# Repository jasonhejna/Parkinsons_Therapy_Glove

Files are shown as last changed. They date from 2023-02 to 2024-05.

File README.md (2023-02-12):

# Parkinsons_Therapy_Glove
Open Source Hardware design for Vibrotactile Coordinated Reset (vCR) Gloves.

open source hardware logo

# Intro

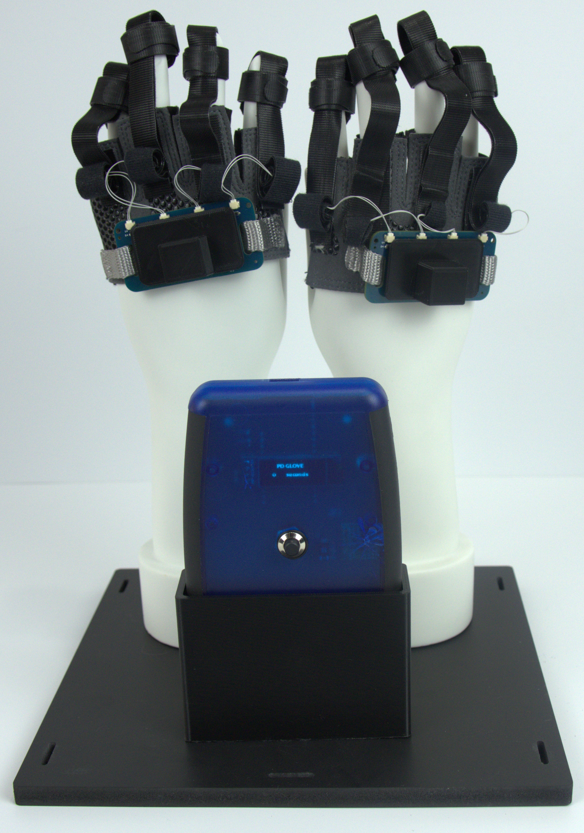
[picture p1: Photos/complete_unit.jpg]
Project Photo


Abnormal synchronization of neuronal activity in dopaminergic circuits is related to motor impairment in Parkinson’s disease (PD). Vibrotactile coordinated reset (vCR) fingertip stimulation aims to counteract excessive synchronization and induce sustained unlearning of pathologic synaptic connectivity and neuronal synchrony.

Vibrotactile Coordinated Reset delivers vibratory stimulation to the fingertips of each hand. A specific pattern of vibration to each fingertip is delivered which theoretically disrupts abnormal synchrony in the brain.

This project provides instructions to build your own vCR Glove. Including Bill of Materials, Instructions, CAD Files, Circuit Board design files, and Firmware.

# Control Box

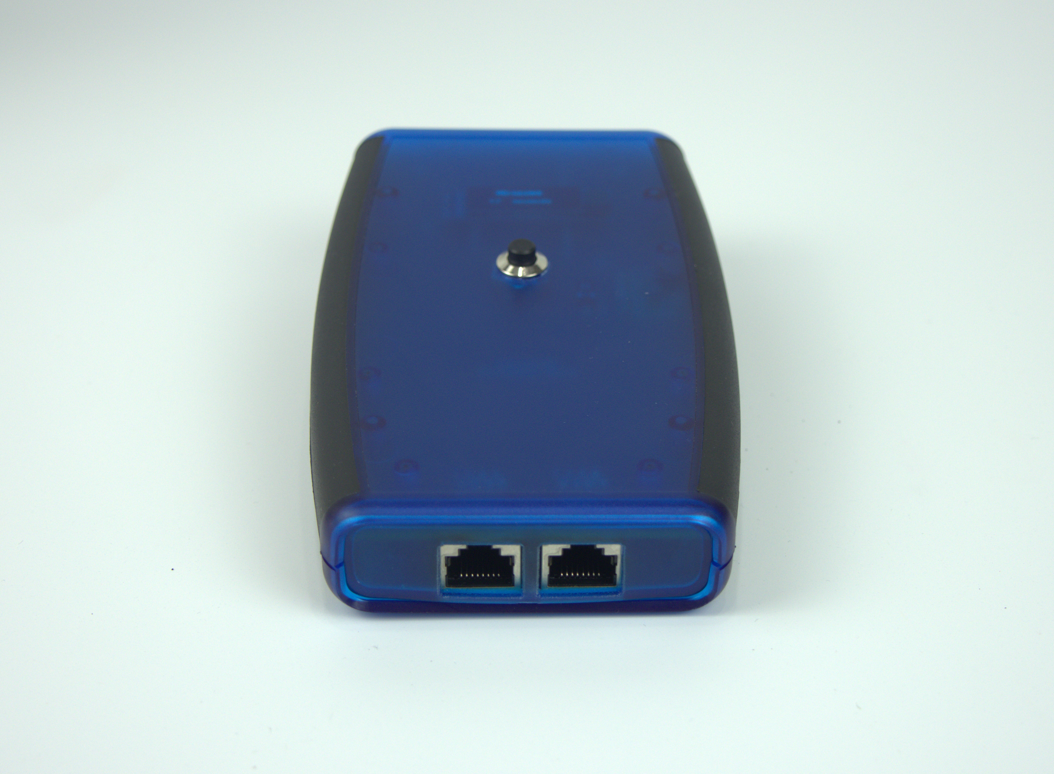
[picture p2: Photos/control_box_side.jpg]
Project Photo

Project Photo
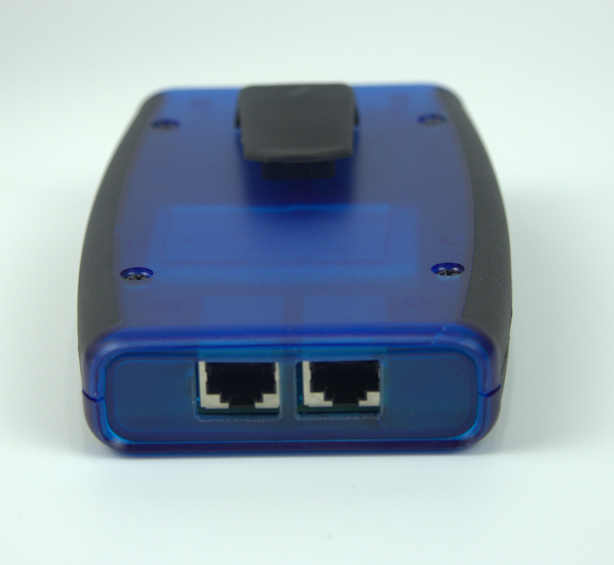
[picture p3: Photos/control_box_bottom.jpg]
Project Photo

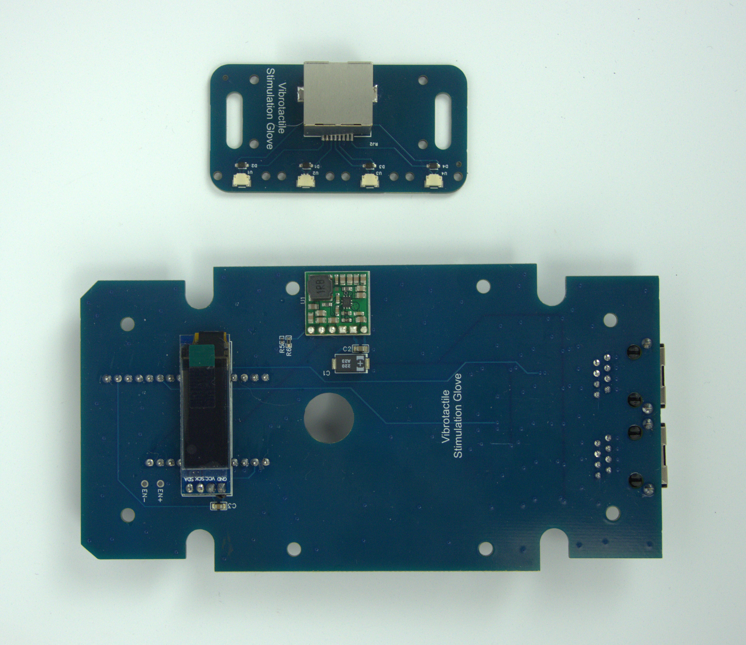
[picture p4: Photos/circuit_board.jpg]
Project Photo

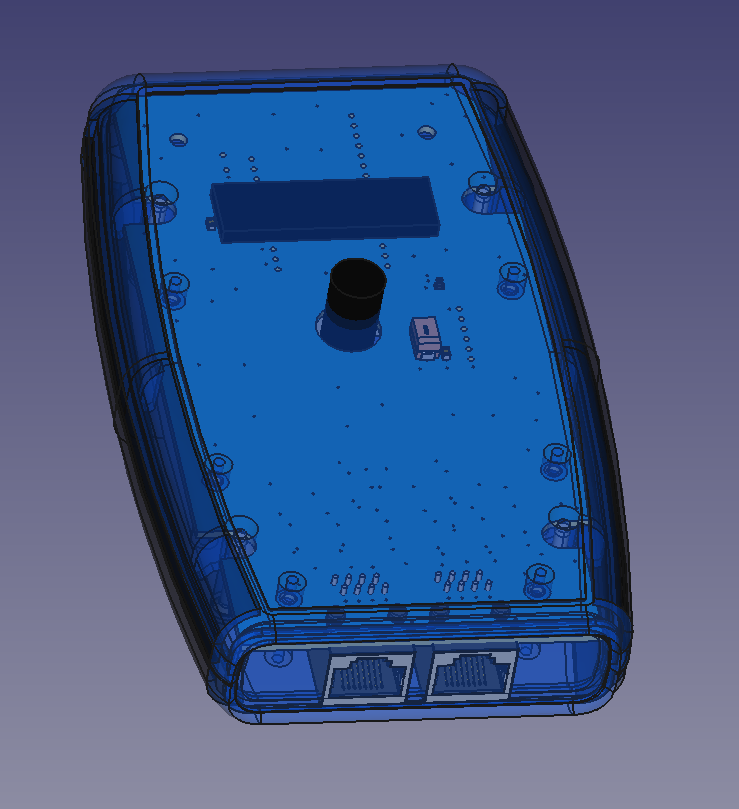
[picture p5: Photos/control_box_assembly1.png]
Project Photo

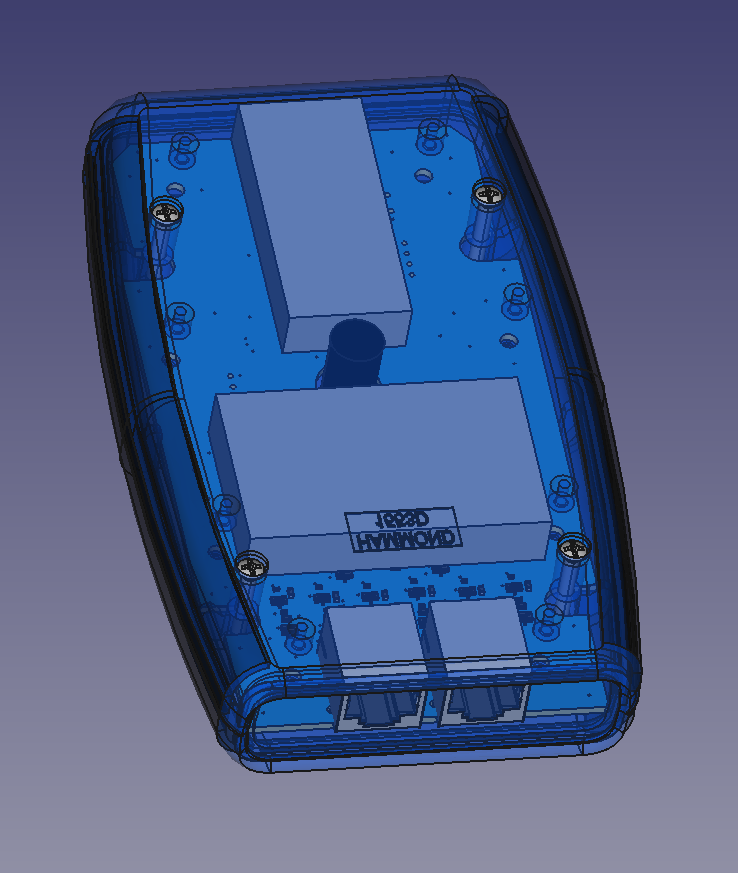
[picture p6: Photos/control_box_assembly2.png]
Project Photo

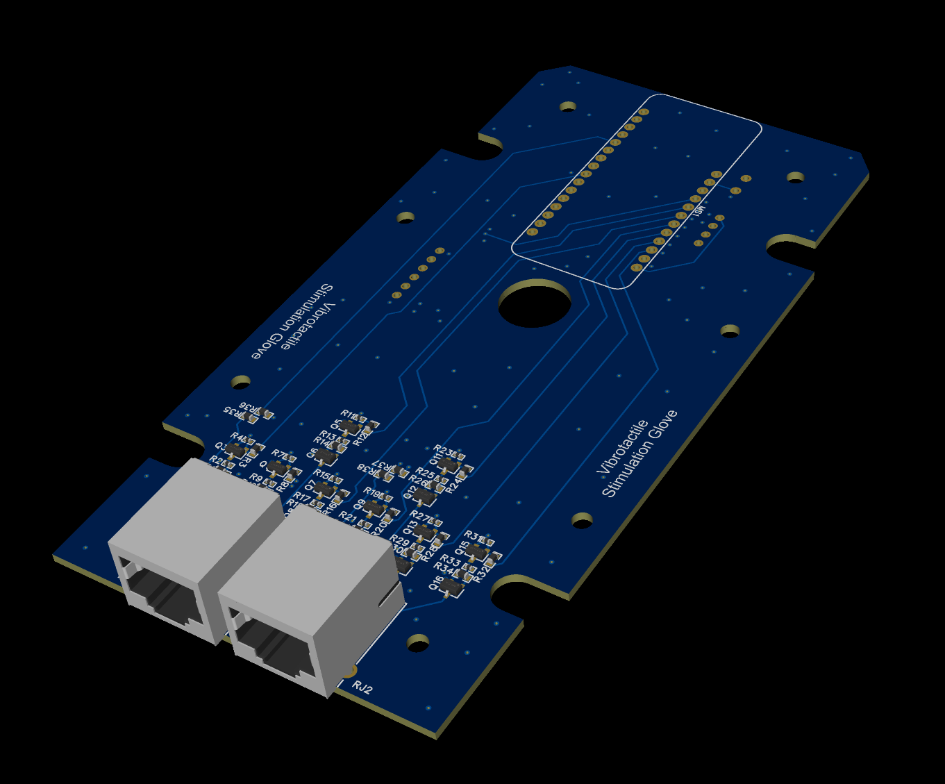
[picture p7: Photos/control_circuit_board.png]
Project Photo


## Build Steps
1) You will need to have a manufacturer create the Printed Circuit Boards (PCB). Upload the Gerber file to the manufacturer: Control_Box\Electronics\Control_Box_Gerber.zip.  I recommend having your circuit board assembled with all the components. Use the PickAndPlace, and BOM files for assembly. JLCPCB.com is a good choice for manufacturer.
2) You will also need to order parts. See the Bill of Materials.
3) You will need to solder on the Feather Microcontroller, Screen, and Boost Converter. These parts are easy to solder 2.54 through hole components.
4) You will need to solder on the switch to the two pins labeled EN+ and EN-.
5) You will need to cut a hole for the switch, and cut a slot for the USB charging cable. These cuts may be made with hand tools. You may also find laser cutter dxf files in Control_Box/Case_Assembly.
6) You will need to flash the provided firmware onto the Feather Microcontroller. Use the Arduino IDE and a USB cable. See Firmware.

## Hardware Bill of Materials
|Part|Part #|Quantity|Manufacturer|URL|
|----|----|----|----|----|
|Custom Printed Circuit Board (See Control_Box/Electronics for design files) ||1|JLCPCB|https://jlcpcb.com/|
|Panel Mount Latching Push Button|CYT1091|1|Cylewet|https://www.amazon.com/Cylewet-Self-Locking-Latching-Button-CYT1091/dp/B075VBV4QH/ref=sr_1_3?keywords=Latching+Switch&qid=1673285409&sr=8-3|
|Case|1553D|1|Hammond Manufacturing|https://www.digikey.com/en/products/detail/hammond-manufacturing/1553DTBUBK/2094890|
|Belt Clip|1599CLIP|1|Hammond Manufacturing|https://www.digikey.com/en/products/detail/hammond-manufacturing/1599CLIP/460760|
|Boost Converter|U3V40F5|1|Pololu|https://www.pololu.com/product/4012|
|0.91 inch OLED LCD Display 128x32|SSD1306|1|Teyleten|https://www.amazon.com/Teyleten-Robot-Display-SSD1306-Raspberry/dp/B08ZY4YBHL/ref=asc_df_B08ZY4YBHL/?tag=hyprod-20&linkCode=df0&hvadid=647248209079&hvpos=&hvnetw=g&hvrand=3522876089040420258&hvpone=&hvptwo=&hvqmt=&hvdev=c&hvdvcmdl=&hvlocint=&hvlocphy=9010937&hvtargid=pla-1597285851745&psc=1&region_id=972485&gclid=CjwKCAiArY2fBhB9EiwAWqHK6iJZr7Km3gjcYjdACghR9q-pTSBiGfFTmBRAXwzSj8zmCsqIJq6RdxoCsYEQAvD_BwE
|Arduino based Feather Microcontroller|2772|1|Adafruit|https://www.adafruit.com/product/2772|
|Battery|2011|1|Adafruit|https://www.adafruit.com/product/2011|
|Screws for holding the Circuit Board|M3 x 8mm|6|Generic||
|Double Sided Adhesive|||Generic||

Note: the battery is necessary for operation.

# Glove Hardware

Project Photo
Project Photo
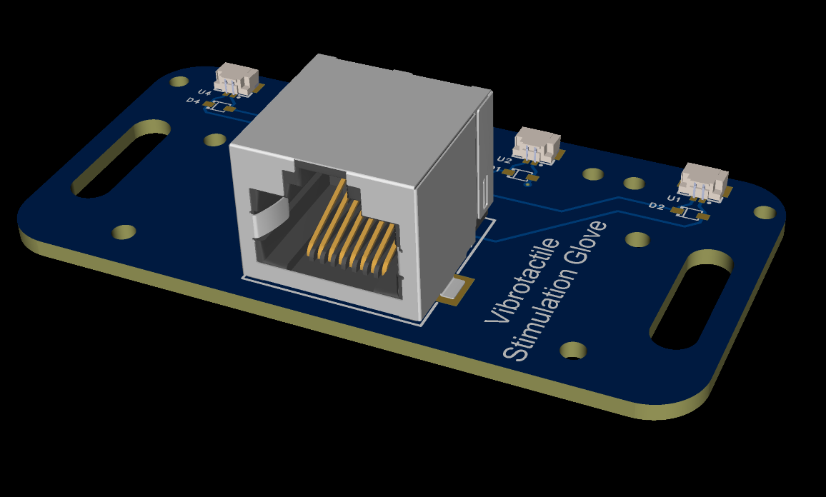
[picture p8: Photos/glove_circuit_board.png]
Project Photo


## Build Steps
1) You will need to send the Printed Circuit Board (PCB) design files to a manufacturer. I recommend having your circuit board assembled with all the components. Upload the Gerber file to the manufacturer (Glove_Hardware/Electronics/Glove_Gerber.zip).
2) Create cables by soldering or crimping the JST Cables onto the ERM Vibration Motor cables. You will need to make eight cable/motor assemblies.
3) Create the motor/finger mounts. This uses double sided velcro stips. The ERM Vibration Motor and cable is placed between two strips, and sewed at the ends. A third piece of velcro strip is used around the finger to ensure a snug fit. You will need to make 8 motor/finger mounts.
4) Cut and attach velcro strips to the glove so that they align with each finger on the glove. Recommend sewing the velcro strips to the gloves, and using adhesive.
5) Leaving extra length for hand movements. Using 1/2-inch Paracord, sew the circuit board to the gloves.
6) Plug the cable assemblies into to the circuit board.
7) Plug an ethernet cable between the glove and control box.
8) Optional. You can 3D print covers for the circuit boards. See Glove_Hardware/glove_PCB_cover.stl.

## Bill of Material

|Part|Part #|Quantity|Manufacturer|URL|
|----|----|----|----|----|
|Custom Printed Circuit Board (See Control_Box/Electronics) ||2|JLCPCB|https://jlcpcb.com/|
|ERM Vibration Motor|1637|8|Pololu|https://www.pololu.com/product-info-merged/1637|
|JST Cables|A02SUR02SUR32W152A|8|JST|https://www.digikey.com/en/products/detail/jst-sales-america-inc/A02SUR02SUR32W152A/6009353|
|Fingerless gloves|F019-BK-M|1|Fit Four|https://www.amazon.com/dp/B06X6NCYP1?psc=1&ref=ppx_yo2ov_dt_b_product_details|
|1/2-inch Paracord|10 X FLTNYLWEB12-SILVER|1|PARACORD PLANET|https://www.amazon.com/dp/B08DZ5GG8W?psc=1&ref=ppx_yo2ov_dt_b_product_details|
|Velcro Strips|91140|1|Velcro Brand|https://www.amazon.com/dp/B001E1Y5O6?psc=1&ref=ppx_yo2ov_dt_b_product_details|
|Ethernet Cable| |2|UGREEN|https://www.amazon.com/dp/B0875NB89J?psc=1&ref=ppx_yo2ov_dt_b_product_details|
|Thread for Sewing| |1|Generic| |
|Adhesive| |1|Generic| |

# Display Case (optional)

Project Photo

## Build Steps
1) Assemble the case using the provided components.
2) Mount the Mannequin Hand Display Stands to the board. I used two screws in each hand.
3) There is a stand for the Control Box which can be 3D printed. See Display_Case_Hardware\control_box_holder.stl. I used three screws to mount the control box holder.

## Bill of Materials

|Part|Part #|Quantity|Manufacturer|URL|
|----|----|----|----|----|
|Mannequin Hand Display Stands| |1|Taotenish|https://www.amazon.com/dp/B07YR2G1NX?psc=1&ref=ppx_yo2ov_dt_b_product_details|
|Display Case|8x8x12 inch 20x20x30 cm|1|KOLIPI|https://www.amazon.com/dp/B0B3WMXPKL?ref=ppx_yo2ov_dt_b_product_details&th=1|

# Editors
You may edit the Electronic design files using a PCB editing software called easyEDA. This project can be accessed on EasyEDA at: https://pro.easyeda.com/editor#id=4203400eb7db434e9a89eb5de0ddfd4a

The CAD files are in FreeCAD format and published in the /Control_Box and /Glove_Assembly folders.

# Attribution

The construction of this project would not be possible without the hard work and dedication of the research team that created Vibrotactile coordinated reset (vCR), conducted the research, and generally worked on this endeavor.

# Author

* Jason Hejna - Product Development Engineer

# Final Thoughts

All design files are provided completely free of charge. I welcome any feedback or improvements to the design. Please submit feedback through Github.

Please notify me if parts go out of stock. I would like to update out of stock parts.

To anyone who tries this design. Please let me know how it goes!

Thank you

# License

This source code is licensed under the Apache-2.0 license found in the LICENSE file in the root directory of this source tree. This project should be considered Open Source Hardware. You are free to use and modify any of the content herein.

Unless otherwise separately undertaken by the Licensor, to the extent possible, the Licensor offers the Licensed Material as-is and as-available, and makes no representations or warranties of any kind concerning the Licensed Material, whether express, implied, statutory, or other. This includes, without limitation, warranties of title, merchantability, fitness for a particular purpose, non-infringement, absence of latent or other defects, accuracy, or the presence or absence of errors, whether or not known or discoverable. Where disclaimers of warranties are not allowed in full or in part, this disclaimer may not apply to You.

To the extent possible, in no event will the Licensor be liable to You on any legal theory (including, without limitation, negligence) or otherwise for any direct, special, indirect, incidental, consequential, punitive, exemplary, or other losses, costs, expenses, or damages arising out of this Public License or use of the Licensed Material, even if the Licensor has been advised of the possibility of such losses, costs, expenses, or damages. Where a limitation of liability is not allowed in full or in part, this limitation may not apply to You.

The disclaimer of warranties and limitation of liability provided above shall be interpreted in a manner that, to the extent possible, most closely approximates an absolute disclaimer and waiver of all liability.

open source hardware logo

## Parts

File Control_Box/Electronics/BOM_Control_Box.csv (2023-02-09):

No. | Quantity | Comment | Designator | Footprint | Value | Manufacturer Part | Manufacturer | Supplier Part | Supplier | LCSC Price | LCSC Stock | JLCPCB Price | JLCPCB Stock | Datasheet | Device | JLCPCB Part Class | LCSC Part Name | Name | Unique ID | Resistance | link
1 | 1 | 220uF | C1 | CAP-SMD_L7.3-W4.3-FD |  | 10TPB220M | PANASONIC(松下) | C242173 | LCSC | 1.4812 | 1149 | 9.31 | 557 |  | 10TPB220M | Extended Part |  | 220uF | ggefb66db9da985fa0a
2 | 2 | 2.2uF | C2,C3 | C0805 |  | CL21A225KAFNNNE | SAMSUNG(三星) | C87994 | LCSC | 0.0170 | 820911 | 0.107 | 385176 |  | CL21A225KAFNNNE | Extended Part |  | 2.2uF | gge1a06ba7d37b3afd1,gge46e4a037fbfb9242
3 | 1 | OLED-128x32 | EKRAN1 | OLED-128X32 |  |  |  |  |  |  |  |  |  |  | OLED-128x32 |  |  | OLED-128x32 | gge044529670250cb18
4 | 1 | FEATHERWING_NOSCREW | MS1 | FEATHERWING_NO_SCREW |  |  |  |  |  |  |  |  |  |  | FEATHERWING_NOSCREW |  |  | FEATHERWING_NOSCREW | gge0b1f5ab786c41376
5 | 8 | MMBT3904_C84104 | Q1,Q3,Q5,Q7,Q9,Q11,Q13,Q15 | SOT-23-3_L2.9-W1.3-P1.90-LS2.4-BR |  | MMBT3904 | ST(先科) | C84104 | LCSC |  |  | 0.0602 | 14817 |  | MMBT3904 | Extended Part |  | MMBT3904_C84104 | gge0d8f3384ea90c7eb,gge7a08e0e46a781eb4,gge478dc22ffe3ca8c7,gge4665e3497868fa47,gge14039e7fc573214c,gged5d5b23e4e6ef882,ggee2e4628fe4e2b352,ggef5bf92d5a9ef5d9f
6 | 8 | SI2301CDS-T1-GE3 | Q2,Q4,Q6,Q8,Q10,Q12,Q14,Q16 | SOT-23-3_L3.0-W1.7-P0.95-LS2.9-BR |  | SI2301CDS-T1-GE3 | VISHAY(威世) | C10487 | LCSC |  |  | 0.486 | 152709 |  | SI2301CDS-T1-GE3 | Basic Part |  | SI2301CDS-T1-GE3 | gge3ea9f58e1a9d2235,gge38e5560dc2c3958e,gge0185c38df4925a71,gge32537c7c1aede5f6,gge98106f643687806a,gge679073baed65af24,ggec29e948761800ac1,ggeea604fc2c4f0d98f
7 | 8 | 5.1kΩ | R1,R10,R14,R18,R22,R26,R30,R34 | R0603 |  | 0603WAF5101T5E | UNI-ROYAL(厚声) | C23186 | LCSC |  |  | 0.00612 | 2346929 |  | 0603WAF5101T5E | Basic Part |  | 5.1kΩ | gge0e08dae5721967aa,gge1eebddf9433234d1,gge2c73753931f9d155,gge2f105896c2ffab49,gge0569ea8743deffbf,ggeaa26469ff685048f,ggeb6967aa3b093cba2,ggec5a22d11ef3ee535 | 5.1K
8 | 8 | 240 | R2,R9,R13,R17,R21,R25,R29,R33 | R0402 |  | RC0402FR-07240RL | YAGEO(国巨) | C114755 | LCSC | 0.0007 | 894213 | 0.00397 | 439205 |  | RC0402FR-07240RL | Extended Part |  | 240 | gge0dd8dcd77110c2b5,ggea412932cabd9c5ae,ggeb774cabebffb13fc,ggec9dba533525f9deb,ggee83e79d6018652b2,ggee234d4903c11e999,ggee3874f5411e3afd0,ggef620bca2e64ef807 | 240Ω
9 | 8 | 1K | R3,R8,R12,R16,R20,R24,R28,R32 | R0603 |  | RC0603FR-071KL | YAGEO(国巨) | C22548 | LCSC |  |  | 0.0064 | 8842618 |  | RC0603FR-071KL | Extended Part |  | 1K | gge0a6abd6e610a20c9,gge2ded78ec2fb9edbc,gge80f93691236e084b,gge064419a47c78d1c7,ggeb1a6cf13fe8cc19d,ggeb491da9607a06c68,ggedd7d89d986fabf59,ggefbf9b83a19b411b1 | 1kΩ
10 | 8 | 6.8K | R4,R7,R11,R15,R19,R23,R27,R31 | R0402 |  | RC0402JR-076K8L | YAGEO(国巨) | C137847 | LCSC | 0.0027 | 501094 | 0.0168 | 499473 |  | RC0402JR-076K8L | Extended Part |  | 6.8K | gge626e64a32193c4d6,gge6251308beb247644,ggea1c0f7c11c7a8d0c,ggeaf5e3272f7eed8d0,ggeb20474b0b163cf00,ggee325568edbf406da,ggee031622812261daa,ggef78691cabab940e6 | 6.8kΩ
11 | 1 | 1kΩ | R5 | R0402 |  | ERJ2RKF1001X | PANASONIC(松下) | C242161 | LCSC |  |  | 0.0379 | 82769 |  | ERJ2RKF1001X | Extended Part |  | 1kΩ | gge365197d47bb9c1b3 | 1K
12 | 1 | 100kΩ | R6 | R0603_NEW |  | ERJ3EKF1003V | PANASONIC(松下) | C189597 | LCSC | 0.0078 | 242750 | 0.0487 | 68654 |  | ERJ3EKF1003V | Extended Part |  | 100kΩ | ggeff73743931110229 | 100K
13 | 2 | 47kΩ | R35,R38 | R0603 |  | 0603WAF4702T5E | UNI-ROYAL(厚声) | C25819 | LCSC |  |  | 0.00657 | 1968208 |  | 0603WAF4702T5E | Basic Part |  | 47kΩ | gge40aad60bb57603be,gge06469131e3f9cd7b | 47K
14 | 2 | 33K | R36,R37 | R0603 |  | RC0603FR-0733KL | YAGEO(国巨) | C126359 | LCSC | 0.0012 | 512800 | 0.00749 | 249861 |  | RC0603FR-0733KL | Extended Part |  | 33K | gge35f5d87f0bcb1737,ggef8a6432b7912eec9 | 33kΩ
15 | 2 | R-RJ45R10P-B000 | RJ1,RJ2 | RJ45-TH_R-RJ45R10P-B000 |  | R-RJ45R10P-B000 | Shenzhen Cankemeng | C386758 | LCSC | 0.2627 |  | 1.651 | 0 |  | R-RJ45R10P-B000 | Extended Part |  | R-RJ45R10P-B000 | ggea55be19a1e3e3d3d,ggeb44bf9b5ea99e3c0
16 | 1 | U3V40F5 | U1 | U3V40F5 |  | U3V40F5 | Pololu | U3V40F5 |  |  |  |  | 0 |  | U3V40F5 |  |  | U3V40F5 | gge4cbcb20c9828dc29 |  | https://www.pololu.com/product/4012
17 | 2 | WIRE_SOLDER_POINT | U2,U3 | WIRE_SOLDER_POINT |  |  |  |  |  |  |  |  |  |  | WIRE_SOLDER_POINT |  |  | WIRE_SOLDER_POINT | gge8aa853f11ac9839f,ggef3f20beaa0858562

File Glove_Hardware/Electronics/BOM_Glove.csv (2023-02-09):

No. | Quantity | Comment | Designator | Footprint | Value | Manufacturer Part | Manufacturer | Supplier Part | Supplier | LCSC Price | LCSC Stock | JLCPCB Price | JLCPCB Stock | Datasheet | Device | JLCPCB Part Class | LCSC Part Name | Name | Unique ID | Resistance | link
1 | 4 | 1N4148WS T4 | D1,D2,D3,D4 | SOD-323_L1.8-W1.3-LS2.5-RD |  | 1N4148WS | CJ(江苏长电/长晶) | C2128 | LCSC |  |  | 0.0667 | 7820304 |  | 1N4148WS | Basic Part |  | 1N4148WS T4 | gge6,gge7,gge8,gge9
2 | 1 | MJ5688-B111-HR1-C | RJ2 | RJ45-TH_MJ5688-B111-HR1-C |  | MJ5688-B111-HR1-C | Heling(合陵) | C501471 | LCSC | 0.6539 | 734 | 4.11 | 205 | https://atta.szlcsc.com/upload/public/pdf/source/20200325/C501471_CCCA8890611B7886CC8D3331CE0DA9EE.pdf | MJ5688-B111-HR1-C | Extended Part | RJ45 卧贴 不带LED 全包反口 | MJ5688-B111-HR1-C | gge5
3 | 4 | SM02B-SURS-TF(LF)(SN) | U1,U2,U3,U4 | CONN-SMD_SM02B-SURS-TF-LF-SN |  | SM02B-SURS-TF(LF)(SN) | JST | C566239 | LCSC | 0.2409 | 26995 | 1.514 | 10245 | https://atta.szlcsc.com/upload/public/pdf/source/20200826/C566239_A8FBB14050B915565F3B5D1E0D0D12F8.pdf | SM02B-SURS-TF(LF)(SN) | Extended Part | 针座 | SM02B-SURS-TF(LF)(SN) | gge1,gge2,gge3,gge4

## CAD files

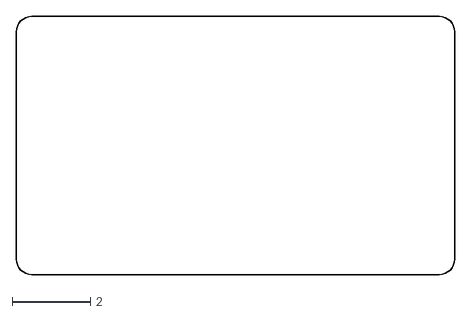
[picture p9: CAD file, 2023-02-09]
Control_Box/Case_Assembly/usb.dxf
11.2 x 6.60

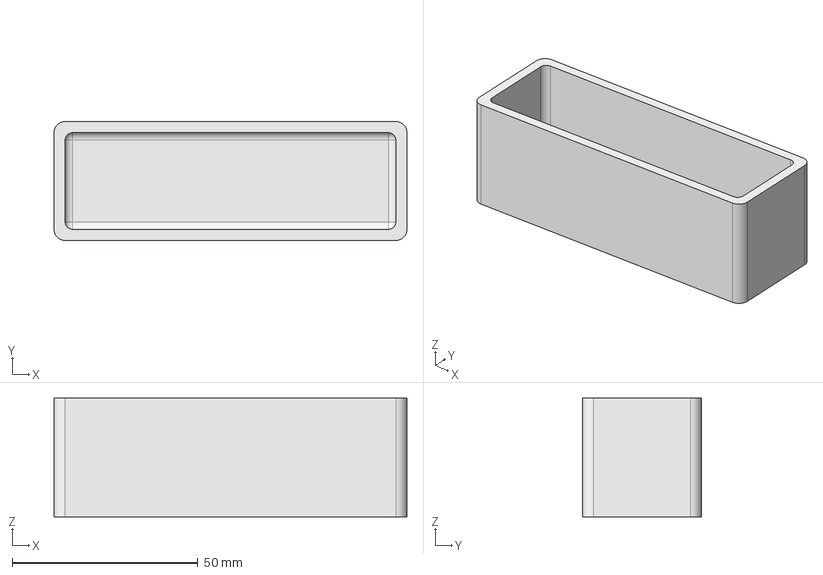
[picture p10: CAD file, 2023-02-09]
Display_Case_Hardware/control_box_holder.FCStd
95.0 x 32.0 x 32.0 mm

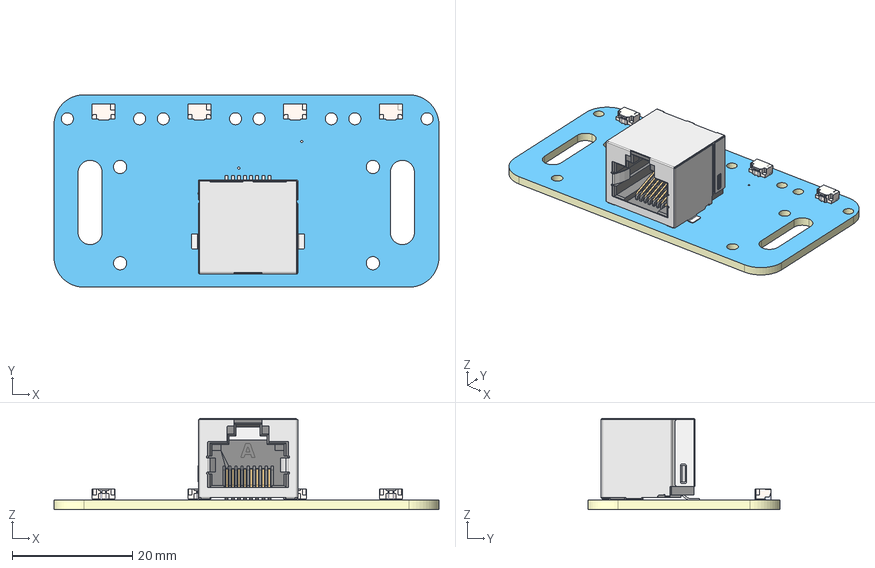
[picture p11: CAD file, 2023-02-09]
Glove_Hardware/Glove_Assembly/3D_PCB2_2023-01-24.step
64.0 x 32.0 x 15.2 mm

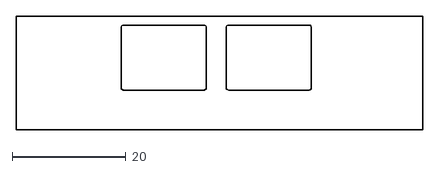
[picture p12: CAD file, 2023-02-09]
Control_Box/Case_Assembly/ethernet.dxf
71.6 x 20.0

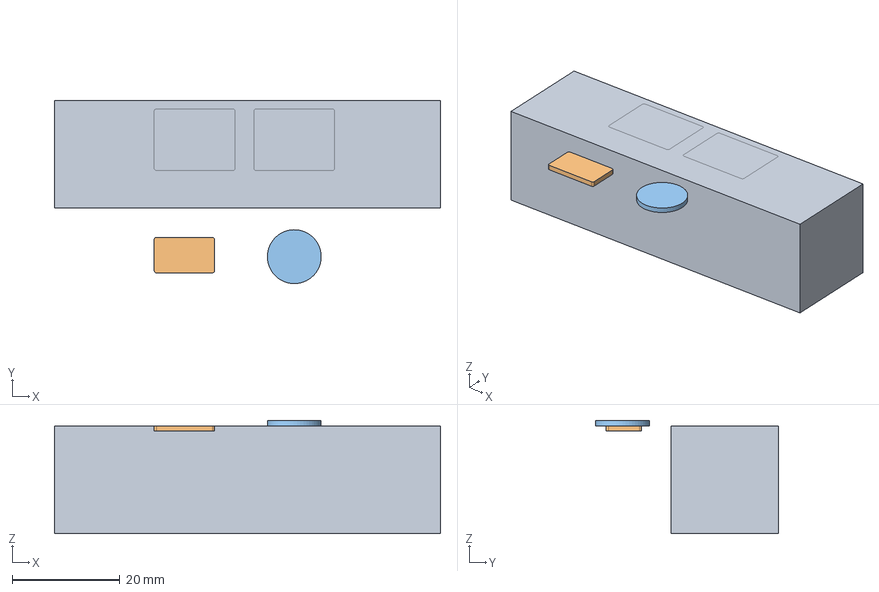
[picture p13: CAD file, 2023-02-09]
Display_Case_Hardware/laser_cut_files.FCStd
71.6 x 34.0 x 21.0 mm
ethernet
usb
switch

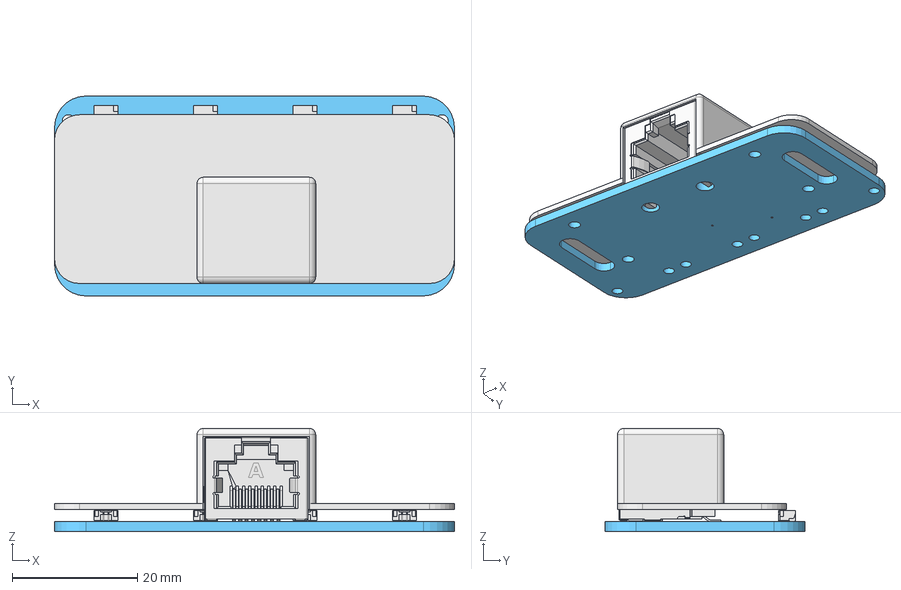
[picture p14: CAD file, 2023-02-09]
Glove_Hardware/Glove_Assembly/glove_top.FCStd
64.0 x 32.0 x 16.5 mm

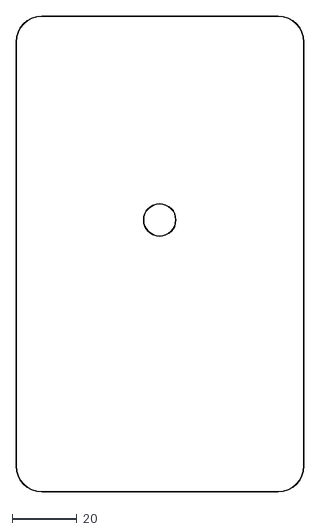
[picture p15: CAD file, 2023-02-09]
Control_Box/Case_Assembly/button.dxf
89.2 x 147.3

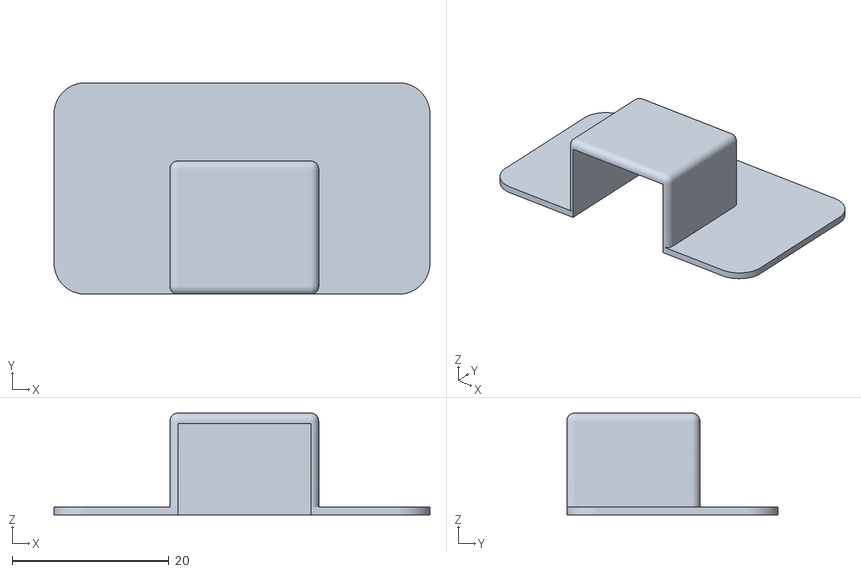
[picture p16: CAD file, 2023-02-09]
Glove_Hardware/Glove_Assembly/glove_PCB_cover.stl
48.0 x 27.0 x 13.0

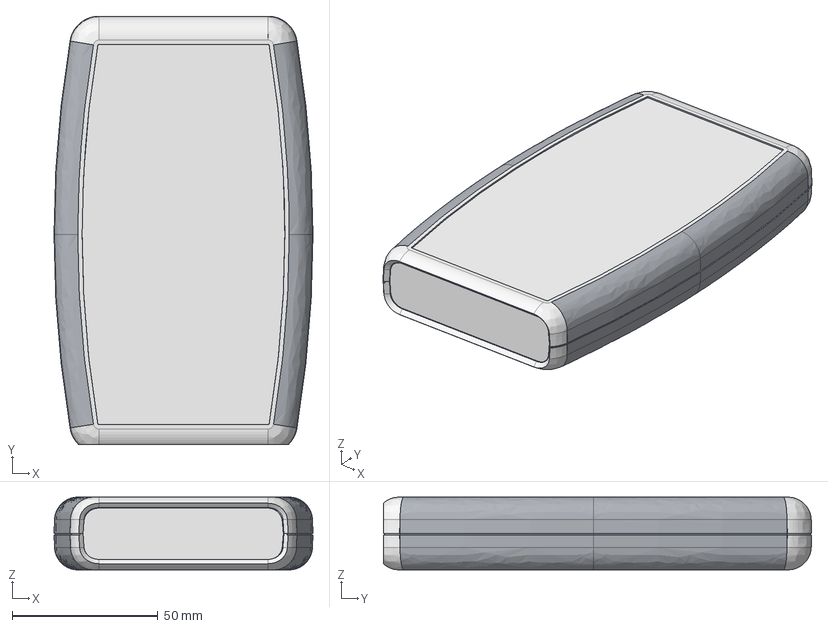
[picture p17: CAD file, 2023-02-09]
Control_Box/Case_Assembly/1553D.stp
89.0 x 147.2 x 25.0 mm
1553D BOTTOM
1553D TOP
1553D FRONT PANEL
1553D PCB
1553D BOTTOM GRIP
1553D TOP GRIP

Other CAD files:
Display_Case_Hardware/control_box_holder.stl

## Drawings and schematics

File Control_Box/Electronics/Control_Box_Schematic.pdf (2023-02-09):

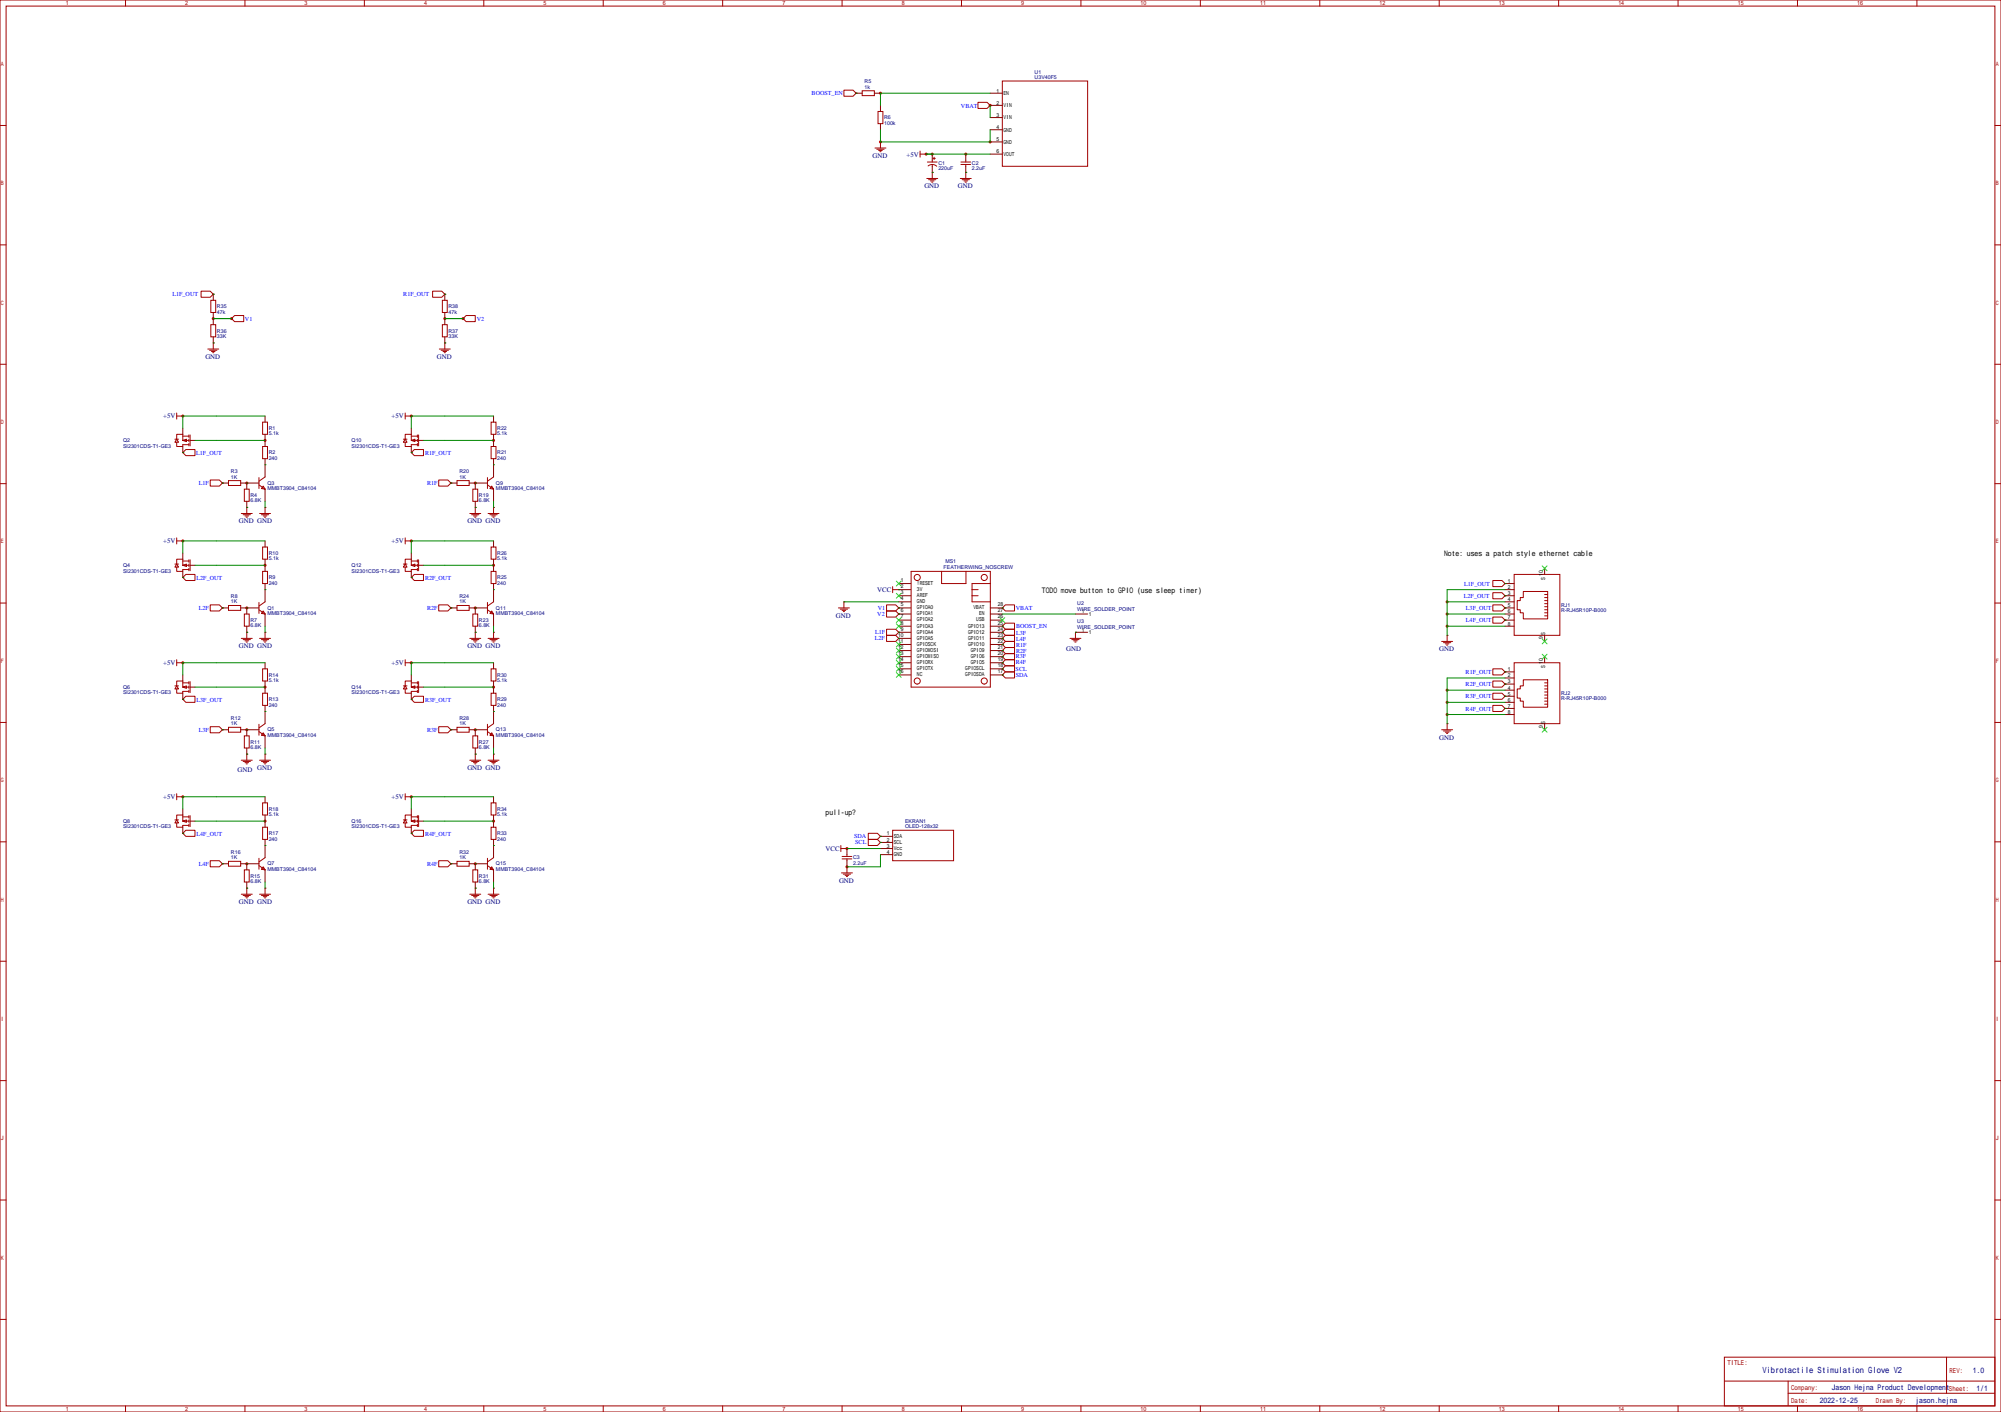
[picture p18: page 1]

Note: uses a patch style ethernet cable

TODO move button to GPIO (use sleep timer)

Jason Hejna Product Development

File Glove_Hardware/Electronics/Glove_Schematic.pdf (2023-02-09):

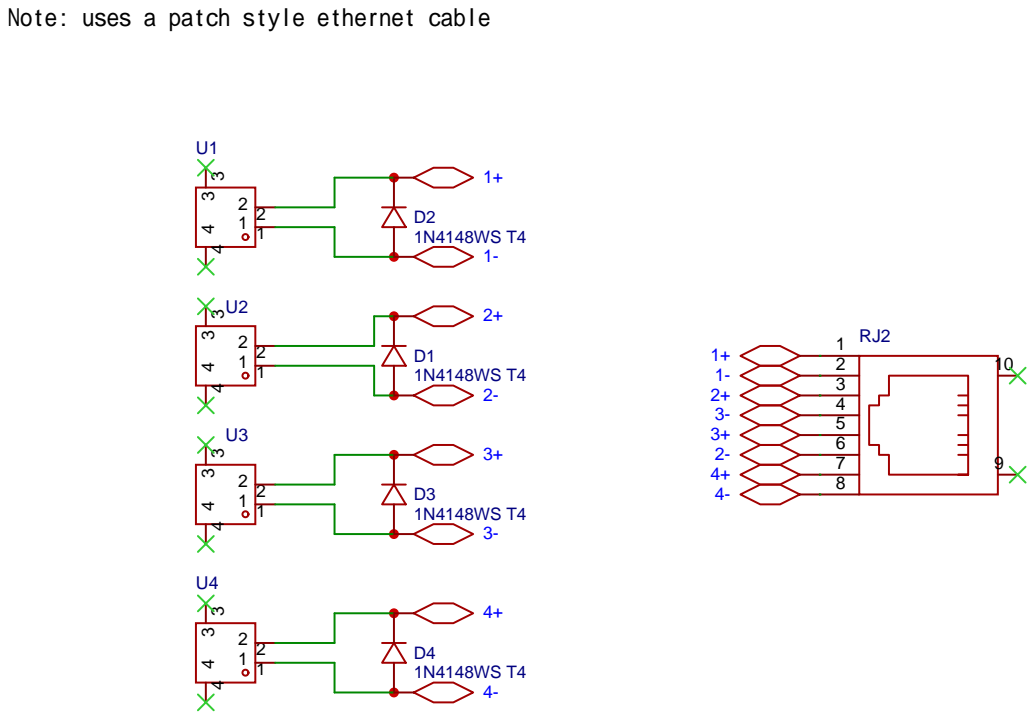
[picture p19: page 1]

Note: uses a patch style ethernet cable

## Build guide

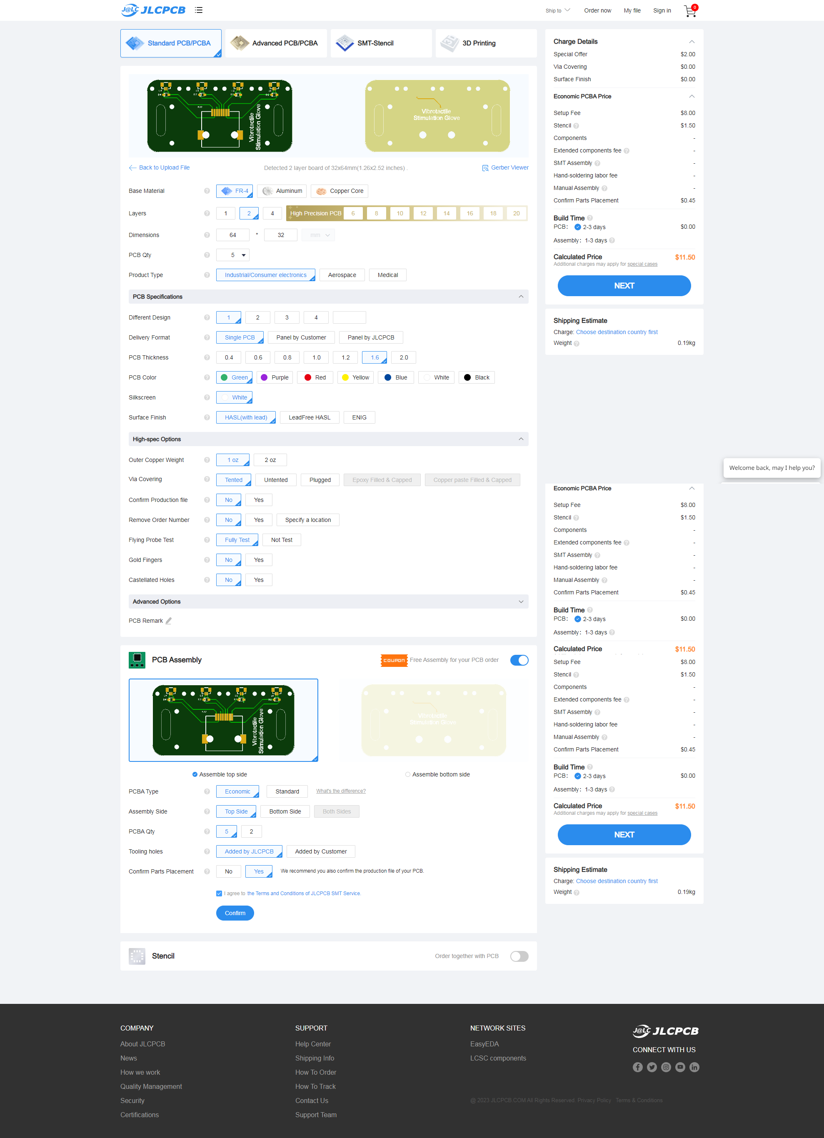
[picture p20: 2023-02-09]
Glove_Hardware/Electronics/jlcpcb_fabrication_settings.png

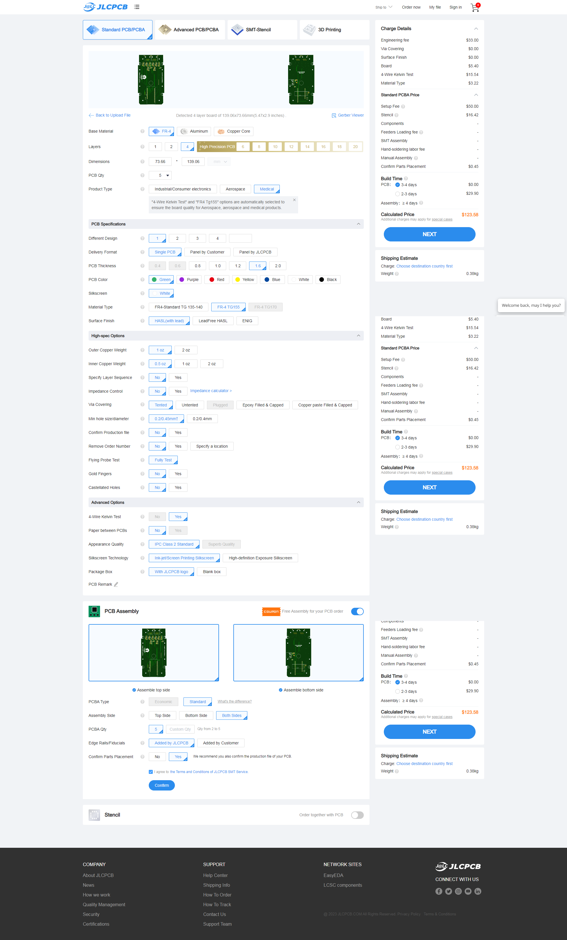
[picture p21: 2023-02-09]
Control_Box/Electronics/jlcpcb_fabrication_settings_control_box.png

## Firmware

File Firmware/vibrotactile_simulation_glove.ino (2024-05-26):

/*
 * Copyright (c) 2023, Jason Hejna
 * All rights reserved.
 * 
 * This source code is licensed under the Apache-2.0 license found in the
 * LICENSE file in the root directory of this source tree. 
 *
 *
 *
 * Project Vibrotactile Coordinated Reset (vCR) Glove Firmware
 * Description: Vibrotactile Coordinated Reset delivers vibratory stimulation to the fingertips of each hand. A specific pattern of vibration to each fingertip is delivered which theoretically disrupts abnormal synchrony in the brain.
 * Author: Jason Hejna
 * Date: 1/19/2023
 */

#include <Arduino.h>
#include <U8g2lib.h>
#include <Wire.h>

// screen lib setup
U8G2_SSD1306_128X32_UNIVISION_F_HW_I2C u8g2(U8G2_R0, /* reset=*/U8X8_PIN_NONE, /* clock=*/SCL, /* data=*/SDA);  // pin remapping with ESP8266 HW I2C

#define boost_en 13
#define L1F A4
#define L2F A5
#define L3F 12
#define L4F 11
#define R1F 10
#define R2F 9
#define R3F 6
#define R4F 5

// time tracking
unsigned long StartTime = millis();
unsigned long CurrentTime = millis();
unsigned long ElapsedTime = CurrentTime - StartTime;
unsigned long seconds;
unsigned long minutes;
char time_str[8];

//bool active = true;
int random_numbers[] = { 0, 1, 2, 3 };
int inter_stimulus_jitter = random(51000, 82332);
int cumulative_jitter;
int active_pinout1;
int active_pinout2;
int sequence = 0;
int vCR_sequence = 0;
uint8_t pulse = 0;

void setup() {
  pinMode(L1F, OUTPUT);
  pinMode(L2F, OUTPUT);
  pinMode(L3F, OUTPUT);
  pinMode(L4F, OUTPUT);
  pinMode(R1F, OUTPUT);
  pinMode(R2F, OUTPUT);
  pinMode(R3F, OUTPUT);
  pinMode(R4F, OUTPUT);

  pinMode(boost_en, OUTPUT);
  digitalWrite(boost_en, HIGH);

  // display
  u8g2.begin();
  u8g2_prepare();
  update_display();
  u8g2.clearBuffer();
  u8g2.drawStr(10, 10, "PD GLOVE");
  u8g2.sendBuffer();
  delay(2000);
  u8g2.setFont(u8g2_font_luBS08_te);
  u8g2.clearBuffer();
  u8g2.drawStr(30, 0, "PD GLOVE");
  for (int i = 5; i > 0; i--) {
    itoa(i, time_str, 10);
    u8g2.clearBuffer();
    u8g2.drawStr(30, 0, "PD GLOVE");
    u8g2.drawStr(50, 20, time_str);
    u8g2.sendBuffer();
    delay(1000);
  }

  // time
  StartTime = millis();

  // random number generator
  randomSeed(analogRead(0));
  generate_randoms();
}

unsigned long pulse_count = 0;


void loop() {
  // Control Voltage to achieve 3.4V or 250Hz on out 
  for (pulse = 0; pulse < 97; pulse++) {
    digitalWrite(active_pinout1, HIGH);
    digitalWrite(active_pinout2, HIGH);
    delayMicroseconds(900);
    digitalWrite(active_pinout1, LOW);
    digitalWrite(active_pinout2, LOW);
    delayMicroseconds(130);
  }
  sequence++;
  if(sequence > 3) {
    sequence = 0;
    generate_randoms();
    check_report_time();
    vCR_sequence++;
    if(vCR_sequence > 2) {
      vCR_sequence = 0;
      if(cumulative_jitter <= 799992) {
        delayMicroseconds(799992 - cumulative_jitter); // nominal 799992
        delay(1500);
      }
      else{
        delayMicroseconds(1500000 - (799992 - cumulative_jitter)); // nominal 799992
      }
      cumulative_jitter = 0; // Reset cumulative_jitter after handling the delay
    }
  }
  advance_finger();
  inter_stimulus_jitter = random(51000, 82332); // jitter +- 23.5%
  cumulative_jitter += inter_stimulus_jitter;
  delayMicroseconds(inter_stimulus_jitter);  //66.666 ms average without jitter
}

void advance_finger(){
    int random_number = random_numbers[sequence];
    switch (random_number) {
      case 0:
        active_pinout1 = L1F;
        active_pinout2 = R4F;
        break;
      case 1:
        active_pinout1 = L2F;
        active_pinout2 = R3F;
        break;
      case 2:
        active_pinout1 = L3F;
        active_pinout2 = R2F;
        break;
      case 3:
        active_pinout1 = L4F;
        active_pinout2 = R1F;
        break;
    }
}

void generate_randoms() {
  for (int i = 0; i < 4; i++) {
    int n = random(0, 4);
    int temp = random_numbers[n];
    random_numbers[n] = random_numbers[i];
    random_numbers[i] = temp;
  }
}

void check_report_time() {
  CurrentTime = millis();
  ElapsedTime = CurrentTime - StartTime;
  seconds = ElapsedTime / 1000;
  u8g2.clearBuffer();
  u8g2.drawStr(30, 0, "PD GLOVE");
  if (seconds < 60) {
    itoa(seconds, time_str, 10);
    u8g2.drawStr(20, 20, time_str);
    u8g2.drawStr(50, 20, "seconds");
  } else {
    minutes = seconds / 60;
    itoa(minutes, time_str, 10);
    u8g2.drawStr(20, 20, time_str);
    u8g2.drawStr(50, 20, "minutes");
  }
  u8g2.sendBuffer();
}

void update_display() {
  u8g2.clearBuffer();
  u8g2.drawStr(10, 10, "PD GLOVE");
  u8g2.sendBuffer();
}

void u8g2_prepare(void) {
  u8g2.setFont(u8g2_font_ncenB14_tf);
  u8g2.setFontRefHeightExtendedText();
  u8g2.setDrawColor(1);
  u8g2.setFontPosTop();
  u8g2.setFontDirection(0);
}
